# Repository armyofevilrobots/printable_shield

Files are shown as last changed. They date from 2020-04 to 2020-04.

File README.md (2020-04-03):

# Face Shield Mod version RC♥

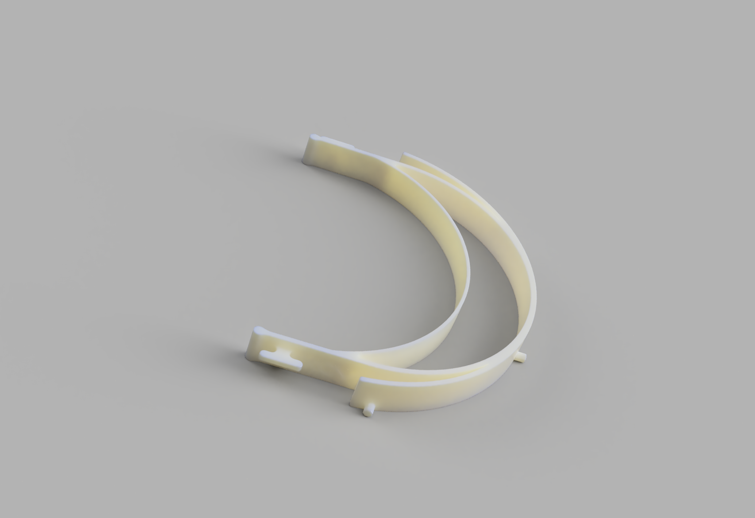
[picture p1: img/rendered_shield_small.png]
Face Shield v3.5


This is a face-shield, not approved for any medical use, but designed
to be similar to the Prusa RC2 face shield, with the following differences:

 - Designed to be high-speed printed (in just over an hour if you have a 0.8mm nozzle)
 - Designed to be modified easily (hence the available [Fusion360](https://www.autodesk.ca/en/products/fusion-360/overview) file
   here: [Face Shield v3.5 Fusion 360 file](https://github.com/armyofevilrobots/printable_shield/blob/master/shield_toggle_wide_v3.5.f3d?raw=true)).
 - Designed to cover the sides and top of the head better, to prevent overspray from
   getting into the users' eyes.

## Usage

### Assembly

Be sure 3D printed head band is correctly oriented - pegs should be along bottom of band.
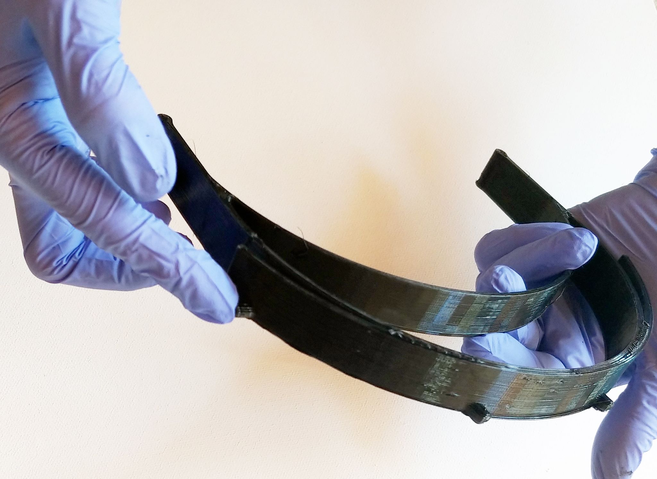
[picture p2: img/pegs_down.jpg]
Pegs are on the bottom


FACE SHIELD snaps onto pegs on top of the TOP  SHIELD tabs, but it’s easiest to attach both FACE  and TOP SHIELD at the same time, starting on one side,  working across the 4 pegs to the other side.
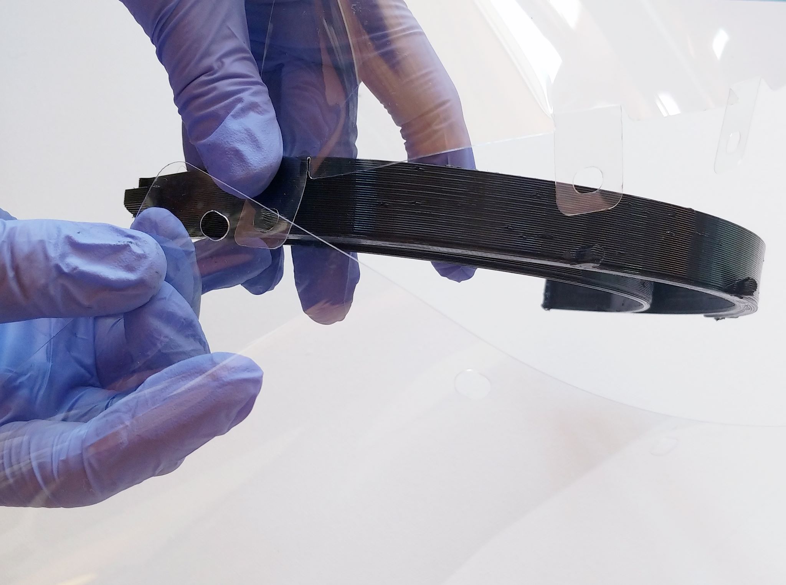
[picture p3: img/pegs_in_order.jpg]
Install starting on one side, and working across


until

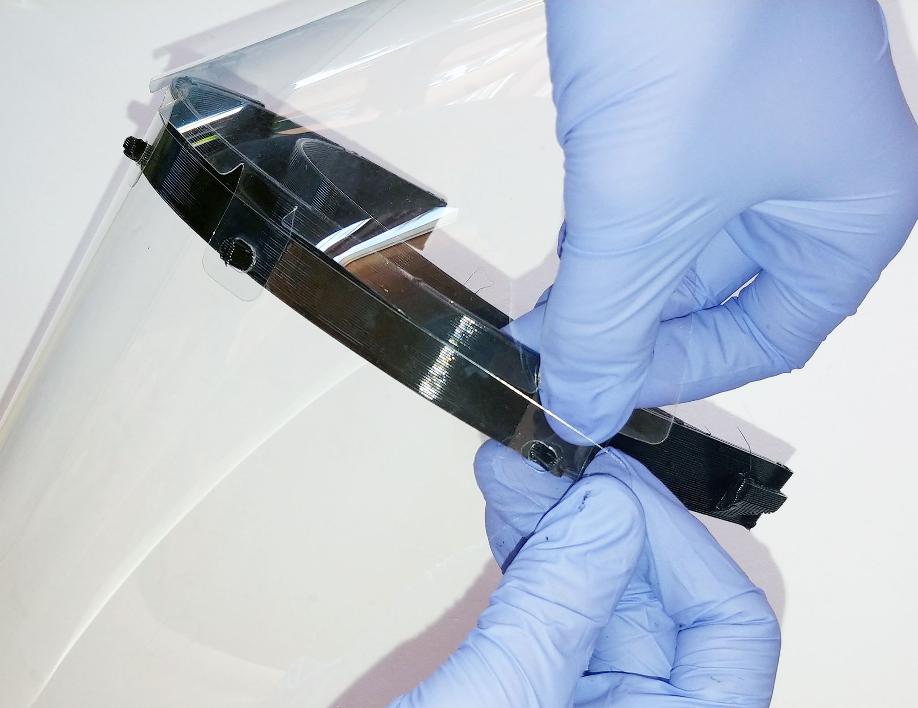
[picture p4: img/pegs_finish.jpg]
You get to the end


Attach elastic strap to fit. Use a buttonhole elastic, available at most sewing stores, cut to length (about 16 inches).

### DISINFECTING INSTRUCTIONS

Masks may be reused but need disinfecting before each use!

Use caution with heat - 3D printed parts  may warp over 100°C

Disassemble to disinfect, and be sure 3D printed parts lay flat or they may warp

## Printing

**Important**: This should only be printed in PETG filament. The sanitization process will usually
completely destroy PLA, and PLA is much more brittle and likely to shatter. Since these masks are kept
next to peoples' eyes, that would be a bad outcome. We have not tested nylon, ABS, nor any other
polyester filaments. We have tested the PETG in an autoclave at low temperature, and with
bleach, and commercial sanitizing solution, without damage. See the cleaning instructions above.

You can view a 3D version of the shield here: [3D Rendered Shield](shield_toggle_wide_v3.5.stl).

I print this with an Ender3 at 250C and averaging 30mm/s speeds. Your mileage may vary. I
am including a 3MF file here: [Face Shield v3.4 FAST](shield_toggle_wide_v3.4_FAST.3mf).

If you want to print using your own slicer/settings, you can get the STL here: [Face Shield v3.5](https://github.com/armyofevilrobots/printable_shield/raw/master/shield_toggle_wide_v3.5.stl)

## Laser Cutting

The shield transparent components are:

 - [The top shield](lasercut_files/TOPSHIELD_wide.pdf)
 - [The face shield](lasercut_files/FACESHIELD_wide.pdf)

There are also SVGs:
Top Shield
Face Shield

These should be cut from 0.005" through 0.010" clear PETG sheet. If you have an amazingly powerful laser, you could use 0.020", but it's very 
finicky on a regular 65W laser engraver, and will likely crack at any size over 0.010".

Since most suppliers are unfamiliar with the chemical name, you can ask graphic design, art, and print houses for Grafix brand art plastic (stock#: K07CP1212-25), or Dura-Lar. These are completely sold out on Amazon at this time, but are probably available locally if you ask around art shops or craft/hobby stores. Don't be tempted to use the thicker sizes unless you have a very high power (150W+) or fiber laser.

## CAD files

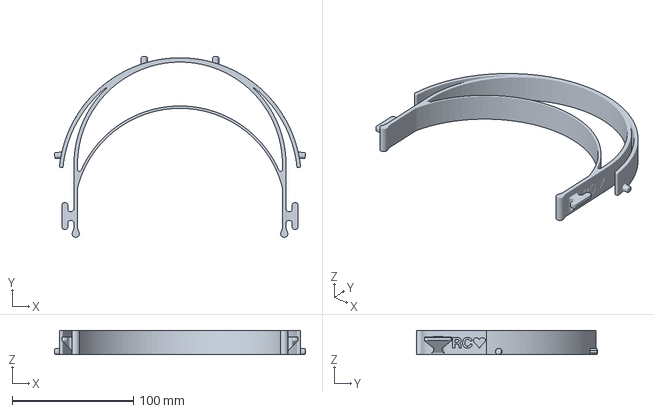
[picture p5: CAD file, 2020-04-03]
shield_toggle_wide_v3.4_FAST.3mf
207.1 x 149.1 x 20.0 mm

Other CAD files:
shield_toggle_wide_v3.5.stl
shield_toggle_wide_v3.5.f3d

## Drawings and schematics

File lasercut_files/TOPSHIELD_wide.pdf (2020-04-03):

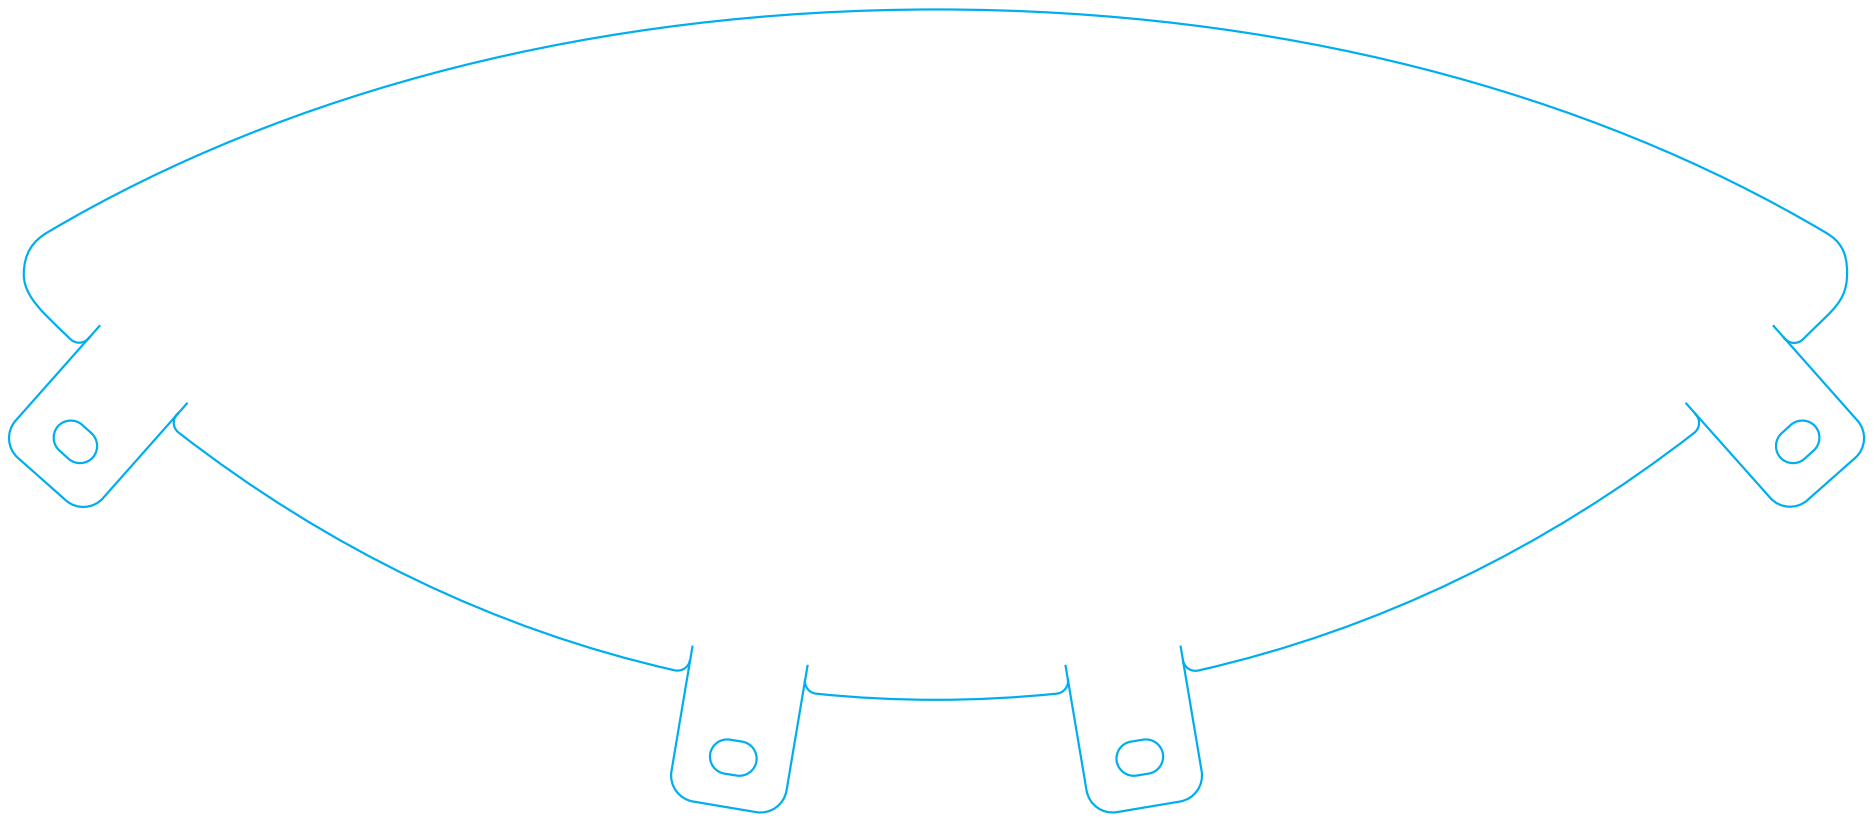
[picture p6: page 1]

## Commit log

2020-04-03 Create repo
    [shield_toggle_wide_v3.4_FAST.3mf, shield_toggle_wide_v3.5.f3d, shield_toggle_wide_v3.5.stl]
2020-04-03 Add laser files.
2020-04-03 Add assembly instructions
